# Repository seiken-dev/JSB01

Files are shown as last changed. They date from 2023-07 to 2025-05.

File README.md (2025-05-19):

# JSB01 -- Johann Sebastian Bachってなに？

<p align="center">
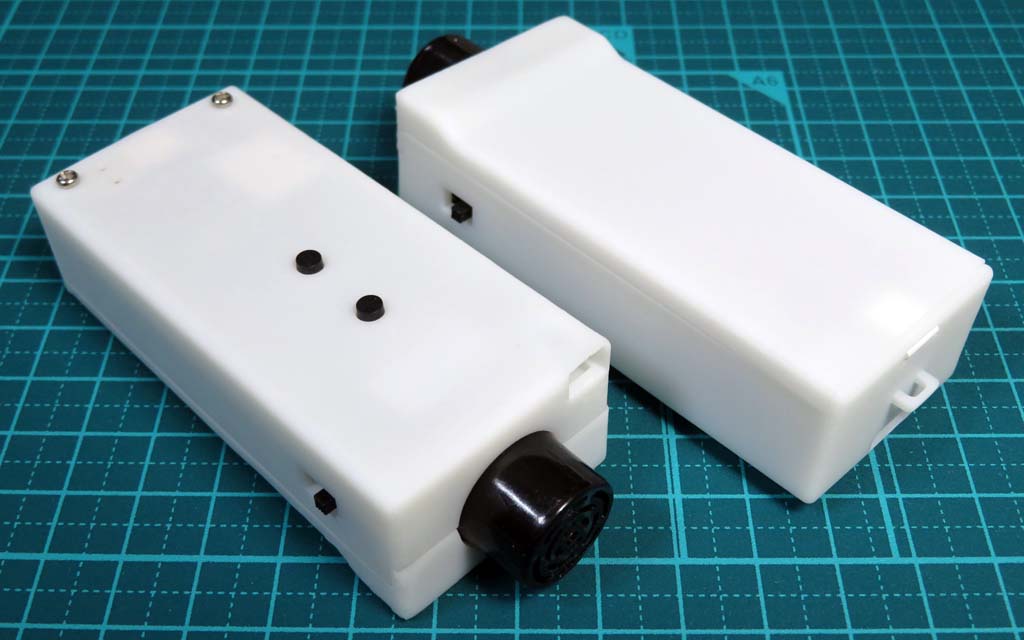
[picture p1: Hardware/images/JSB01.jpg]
JSB01

</p>

視覚障害者の歩行支援デバイスです。距離センサー、地磁気センサー(コンパス)、照度センサーを備え、振動によって情報を伝えます。

## コンテンツ
- **Firmware**<br>
PlatformIOでビルドできるソースコードです(動作テスト用)。[XIAO RP2040](https://wiki.seeedstudio.com/XIAO-RP2040/)(Rev.1)と、基板実装のRP2040(Rev.3)に対応しています。
- **KiCad**<br>
[KiCad](https://www.kicad.org/)のプロジェクトです。Rev.1の**JSB01.kicad_pro**と、Rev.3の**JSB01R3.kicad_pro**の２つのプロジェクトファイルがあります。シンボルとフットプリントは共通です。
- **Blender**<br>
3Dプリントケース作成用のBlenderのプロジェクトファイルと、発注に使用したSTLファイルです。

※ **KiCad**と**Blender**のデータは、**Creative Commons** [**CC BY**](https://creativecommons.org/licenses/by/4.0/legalcode.ja)のライセンスの元で、自由に使用/改変/製作して頂いて構いません。ただし、データや製作物に対しては作者は一切の責任を負いません。

## 各ブランチはなんのため？

* c.mos: c.mosさん作成のコードです。ハードウェアのすべての機能を実装しています
* ATtiny: ATtiny X0Xシリーズをマイコンとして使うブランチ
* ESP32C3: XIAO ESP32C3をマイコンとして使って、esp-idfを開発環境にするブランチ
* RP2040: RP2040あるいは XIAO RP2040を使って、pico-sdkを開発環境にするブランチ
* Experimental: 各種実験ブランチ
* main: そのうちメインになるだろうブランチ

## その他

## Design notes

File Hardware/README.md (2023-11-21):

# JSB01ハードウェア
<p align="center">
JSB01
</p>

視覚障害者の歩行支援デバイスです。距離センサー、地磁気センサー(コンパス)、照度センサーを備え、振動によって情報を伝えます。

# コンテンツ
- **KiCad**<br>
[KiCad](https://www.kicad.org/)のプロジェクトです。Rev.1の**JSB01.kicad_pro**と、Rev.3の**JSB01R3.kicad_pro**の２つのプロジェクトファイルがあります。シンボルとフットプリントは共通です。
- **Blender**<br>
3Dプリントケース作成用のBlenderのプロジェクトファイルと、発注に使用したSTLファイルです。

# 基板の組み立て(Rev.3)
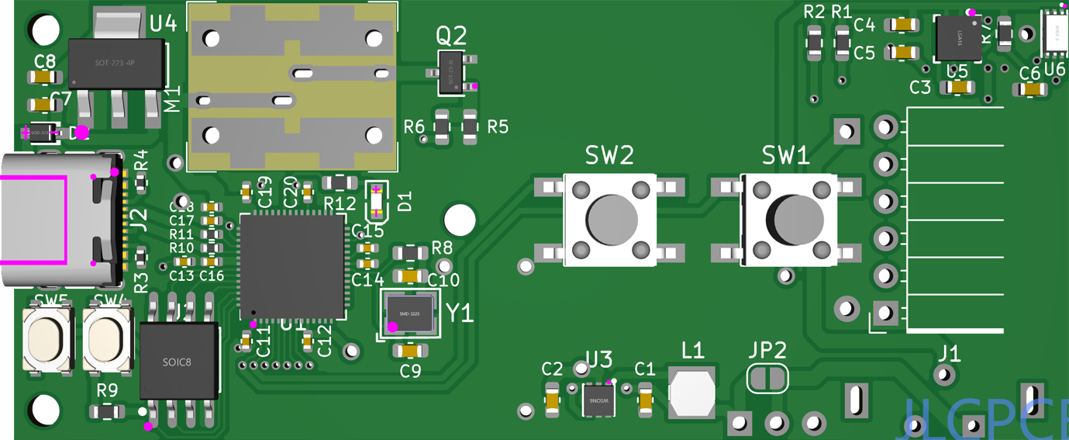
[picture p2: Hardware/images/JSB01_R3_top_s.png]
JSB01_R3_top_s
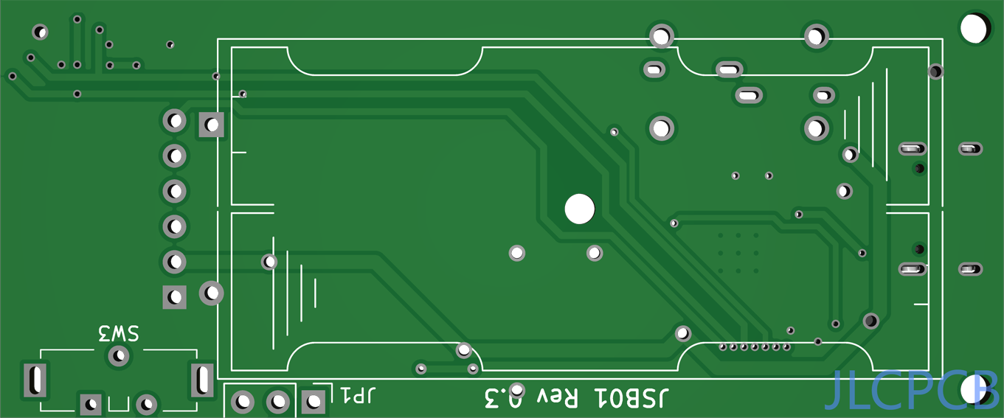
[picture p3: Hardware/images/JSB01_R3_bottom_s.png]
JSB01_R3_bottom_s
  

表面実装部品(SMD)は[JLCPCB](https://jlcpcb.com/)などPCB基板発注業者で実装できます。それ以外にはんだ付けする必要な部品のリストを載せます。

- [リニア振動アクチュエータ LD14](https://akizukidenshi.com/catalog/g/gP-06838/)<br>
こちらもSMDなので、基板業者へ部品を送って実装してもらうのがベストですが、手はんだの場合は、まずリード線をLD14の裏へはんだ付けした上で、リード線を基板の穴から引き出してはんだ付けして固定します。
- [L型ピンソケット(6P)](https://akizukidenshi.com/catalog/g/gC-09862/)<br>
MaxBotixの超音波センサー[MB10XXシリーズ](https://akizukidenshi.com/catalog/g/gM-08238/)を付けるソケットです。超音波センサーの基板側にも、GND～PW端子の6ピンに、ピンヘッダを付ける必要があります。
- [スライドスイッチ(ESD175202)](https://akizukidenshi.com/catalog/g/gP-08944/)
- [単4×2 電池ケース(SN4-2PC)](https://www.marutsu.co.jp/pc/i/65116/)

他に、電流測定用のJP1に3ピンヘッダを付けてジャンパピンを付けるか、JP2のソルダジャンパーをはんだで繋げます。<br>
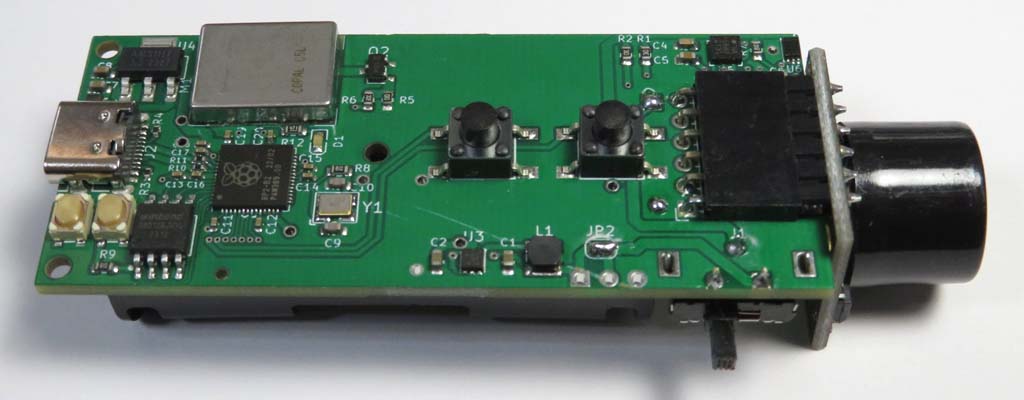
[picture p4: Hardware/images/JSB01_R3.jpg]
JSB01_R3


# 基板の組み立て(Rev.1)
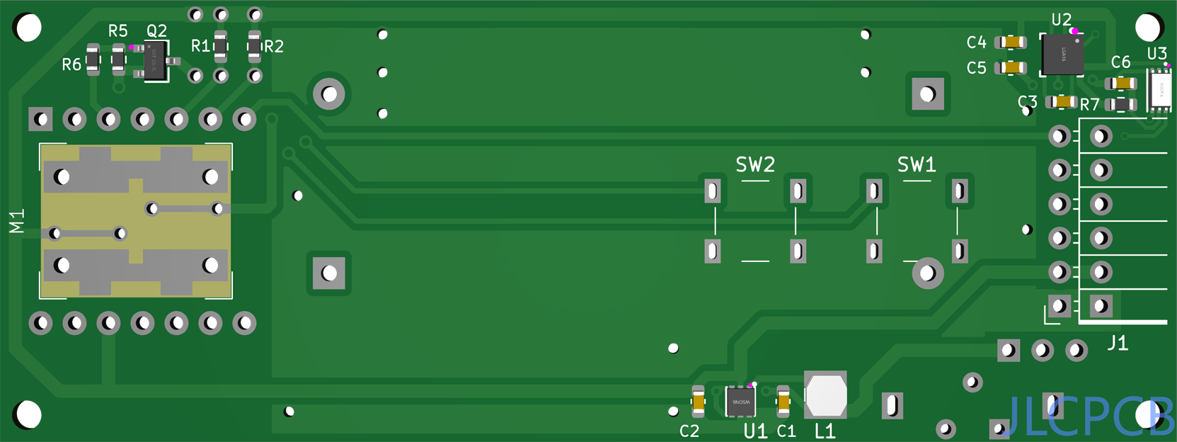
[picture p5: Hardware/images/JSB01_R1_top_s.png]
JSB01_R1_top_s
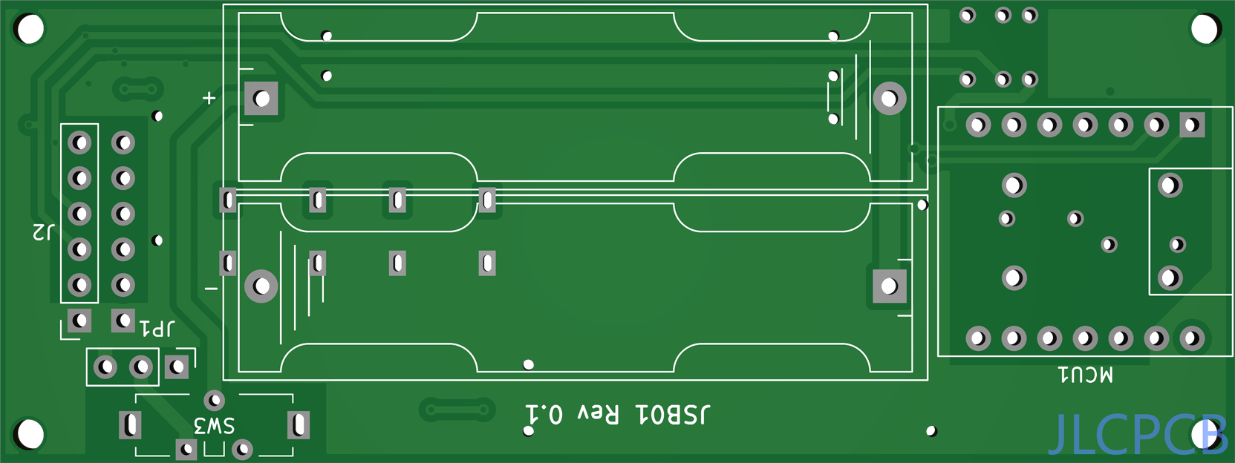
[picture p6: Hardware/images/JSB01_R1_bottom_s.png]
JSB01_R1_bottom_s
  

最初に作った基板です。リビジョンが跳んでいるのは、Rev.2から3Dプリントケースを作ったためで、設計した基板はこの２種類だけです。これは[キャンドゥのケース](https://ec.cando-web.co.jp/item/4582547004810/)に収めるサイズで作りました。[Seeed Studio XIAO](https://wiki.seeedstudio.com/SeeedStudio_XIAO_Series_Introduction/)シリーズが載るソケットと、超音波センサーの他に[ストロベリーリナックス](https://strawberry-linux.com)の[TOFセンサー](https://strawberry-linux.com/catalog/items?code=15311)を付けられます。Rev.3以外に必要な部品のリストを載せます。
- [XIAO RP2040](https://wiki.seeedstudio.com/XIAO-RP2040/)<br>
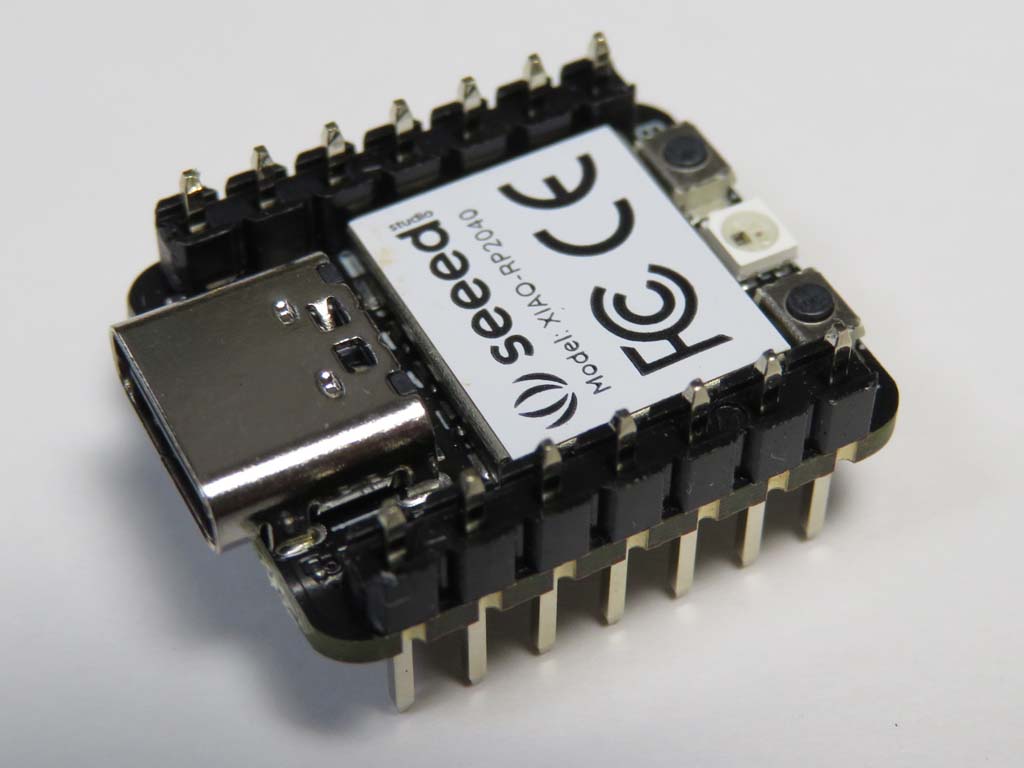
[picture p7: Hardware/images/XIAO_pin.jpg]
XIAO_pin
<br>
高さを低く収めるために、上からピンヘッダを差し込んではんだ付けします。
- [TOFセンサー](https://strawberry-linux.com/catalog/items?code=15311)<br>
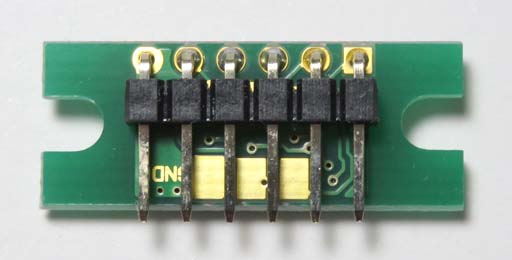
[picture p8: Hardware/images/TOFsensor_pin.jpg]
TOFsensor_pin
<br>
このように、上下逆向きにして裏に[L型ピンヘッダ](https://akizukidenshi.com/catalog/g/gC-12985/)を付けます。
- [シングルピンソケット(低メス)](https://akizukidenshi.com/catalog/g/gC-03138/)<br>
XIAO RP2040とTOFセンサーを載せるために使います。
- [タクトスイッチ×2](https://akizukidenshi.com/catalog/g/gP-03647/)
- [単4電池ボックス×2](https://akizukidenshi.com/catalog/g/gP-02670/)
<br>
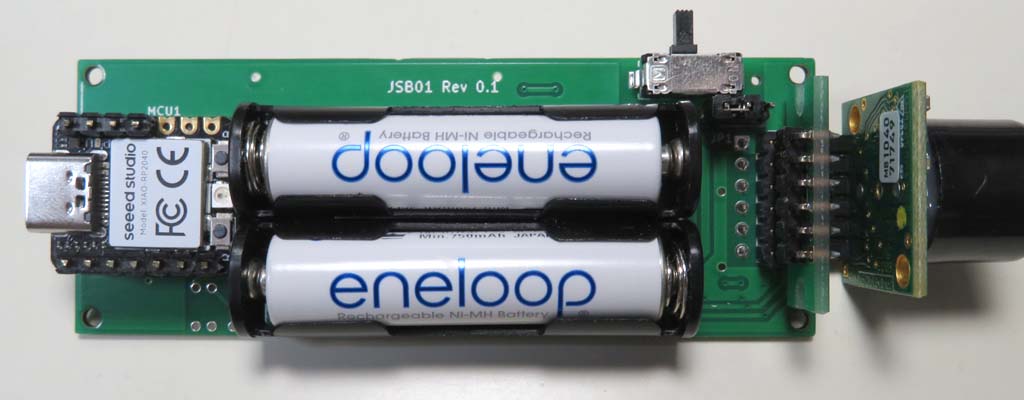
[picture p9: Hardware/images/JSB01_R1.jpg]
JSB01_R1


# 3Dプリントケース
R2(r2)がRev.1基板用、R3(r3)がRev.3基板用のケースです。Rev.1用ケースでは、照度センサー用の穴をチップの上面に開けていましたが、Rev.3では凹面鏡の様に加工して前方からの光を取り入れるようにしました。そのため、凹面鏡の部分を[メタリックの塗料](https://www.mr-hobby.com/ja/product1/category_10/3670.html)で塗る必要があります。

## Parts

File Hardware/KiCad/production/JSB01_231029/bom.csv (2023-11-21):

Designator | Footprint | Quantity | Value | LCSC Part #
C1, C7, C8 | 0603 | 3 | 10uF | C19702
C10, C9 | 0603 | 2 | 33p | C1663
C11, C12, C13, C14, C15, C16, C17, C18, C19, C20 | 0402 | 10 | 100n | C307331
C2 | 0603 | 1 | 22uF | C59461
C3 | 0603 | 1 | 0.22uF | C21120
C4 | 0603 | 1 | 0.1uF | C14663
C5 | 0603 | 1 | 4.7uF | C19666
C6 | 0603 | 1 | 1uF | C15849
D1 | LED0603-RD_GREEN | 1 | LED | C510026
D2 | SOD-323_L1.8-W1.3-LS2.5-RD | 1 | NSR0320MW2T1G | C48192
J1 | PinSocket_1x06_P2.54mm_Horizontal | 1 | MB10XX Sonar
J2 | USB-C-SMD_TYPE-C-16P-1 | 1 | USB_C_Receptacle_USB2.0 | C2982555
JP2 | SolderJumper-2_P1.3mm_Open_RoundedPad1.0x1.5mm | 1 | SolderJumper_2_Open
L1 | IND-SMD_L3.0-W3.0_VLS3010ET | 1 | 3.3μH | C136236
Q2 | AO3400A | 1 | AO3400A | C20917
R1, R2 | 0603 | 2 | 10KΩ | C25804
R10, R11 | 0402 | 2 | 27.4 | C274349
R12 | 0603 | 1 | 470 | C23179
R3, R4 | 0402 | 2 | 5.1K | C25905
R5 | 0603 | 1 | 100KΩ | C25803
R6 | 0603 | 1 | 20KΩ | C4184
R7, R8, R9 | 0603 | 3 | 1K | C21190
SW1, SW2 | Tactile Switch_SMD | 2 | Tactile | C294566
SW4, SW5 | KEY-SMD_4P-L4.2-W3.2 | 2 | SKRPABE010 | C115360
U1 | RP2040-QFN-56 | 1 | RP2040 | C2040
U2 | SOP-8-208mil | 1 | W25Q128JVSIQ
U3 | WSON-6_L2.0-W2.0-P0.65-BL-EP | 1 | TPS61291DRVR | C464809
U4 | SOT-223-3_L6.5-W3.4 | 1 | AMS1117-3.3 | C6186
U5 | LGA-16_L3.0-W3.0-P0.50-BL_SQ | 1 | QMC5883L(0x0D) | C976032
U6 | WSOF-6_L2.6-W1.6-P0.50-TL-EP | 1 | BH1750FVI(0x23) | C78960
Y1 | OSC-SMD_4P-L3.2-W2.5 | 1 | TAXM12M4RLBDDT2T

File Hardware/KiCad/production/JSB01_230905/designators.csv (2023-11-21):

BT1:1
C1:1
C2:1
C3:1
C4:1
C5:1
C6:1
J1:1
J2:1
JP1:1
L1:1
M1:1
MCU1:1
Pad:6
Q2:1
R1:1
R2:1
R5:1
R6:1
R7:1
REF**:4
SW1:1
SW2:1
SW3:1
U1:1
U2:1
U3:1

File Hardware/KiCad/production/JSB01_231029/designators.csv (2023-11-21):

BT1:1
C1:1
C10:1
C11:1
C12:1
C13:1
C14:1
C15:1
C16:1
C17:1
C18:1
C19:1
C2:1
C20:1
C3:1
C4:1
C5:1
C6:1
C7:1
C8:1
C9:1
D1:1
D2:1
J1:1
J2:1
JP1:1
JP2:1
L1:1
M1:1
Q2:1
R1:1
R10:1
R11:1
R12:1
R2:1
R3:1
R4:1
R5:1
R6:1
R7:1
R8:1
R9:1
REF**:2
SW1:1
SW2:1
SW3:1
SW4:1
SW5:1
U1:1
U2:1
U3:1
U4:1
U5:1
U6:1
Y1:1

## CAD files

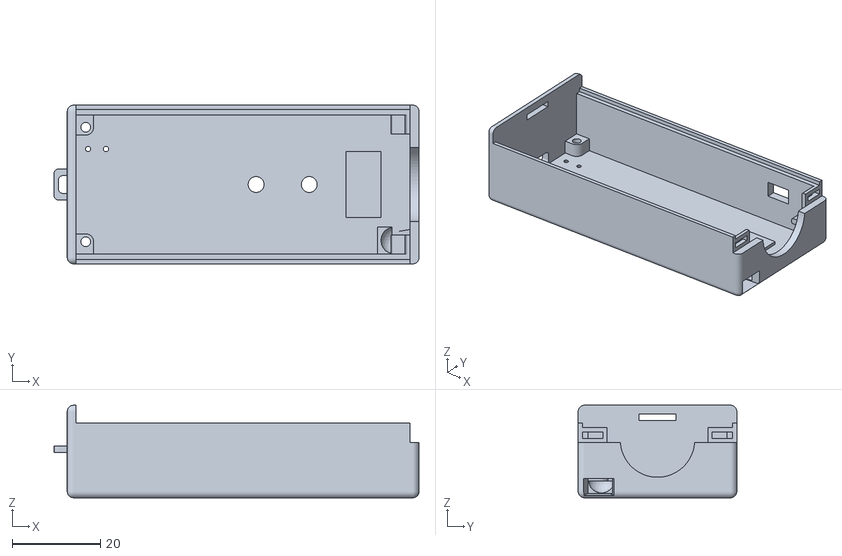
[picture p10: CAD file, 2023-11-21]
Hardware/Blender/JSB01_caseR31.stl
82.8 x 36.0 x 21.0

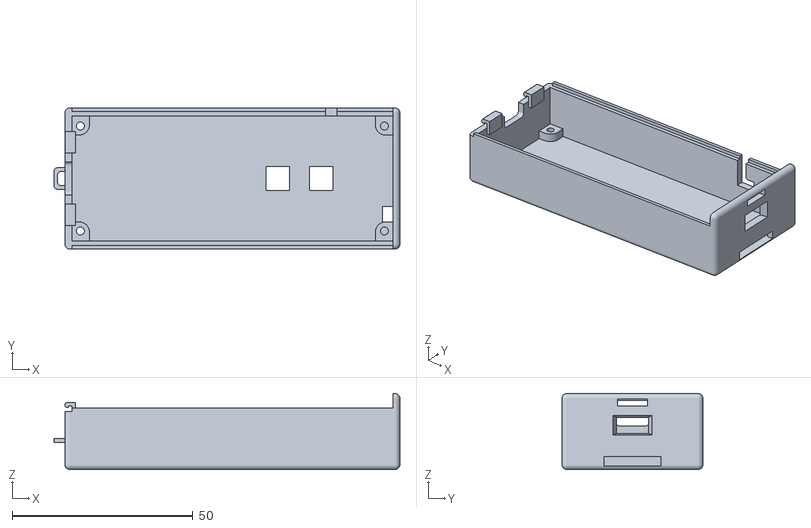
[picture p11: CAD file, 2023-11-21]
Hardware/Blender/JSB01_caseR21.stl
95.6 x 39.0 x 21.0

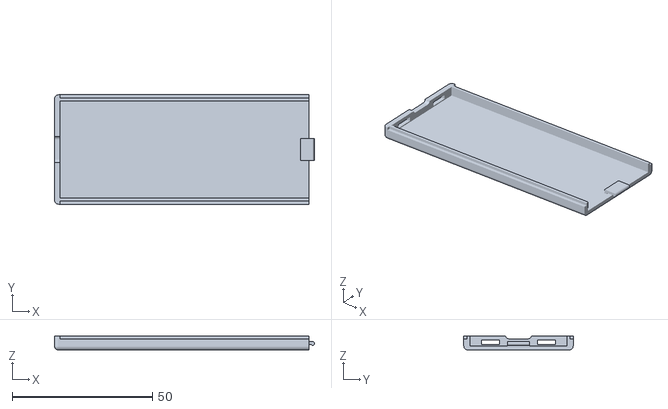
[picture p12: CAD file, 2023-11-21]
Hardware/Blender/JSB01_casetopR2.stl
92.6 x 39.0 x 5.00

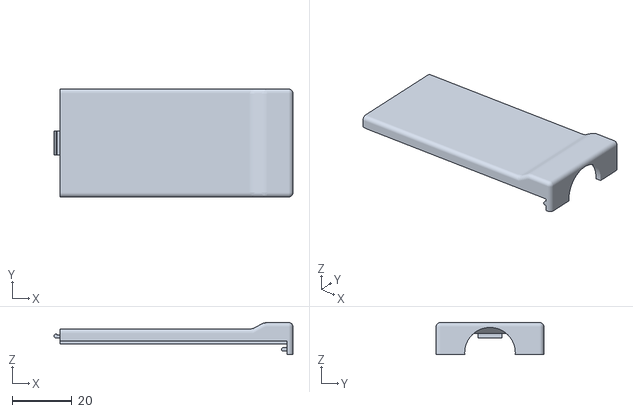
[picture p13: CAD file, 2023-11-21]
Hardware/Blender/JSB01_casetopR31.stl
79.8 x 36.0 x 10.7

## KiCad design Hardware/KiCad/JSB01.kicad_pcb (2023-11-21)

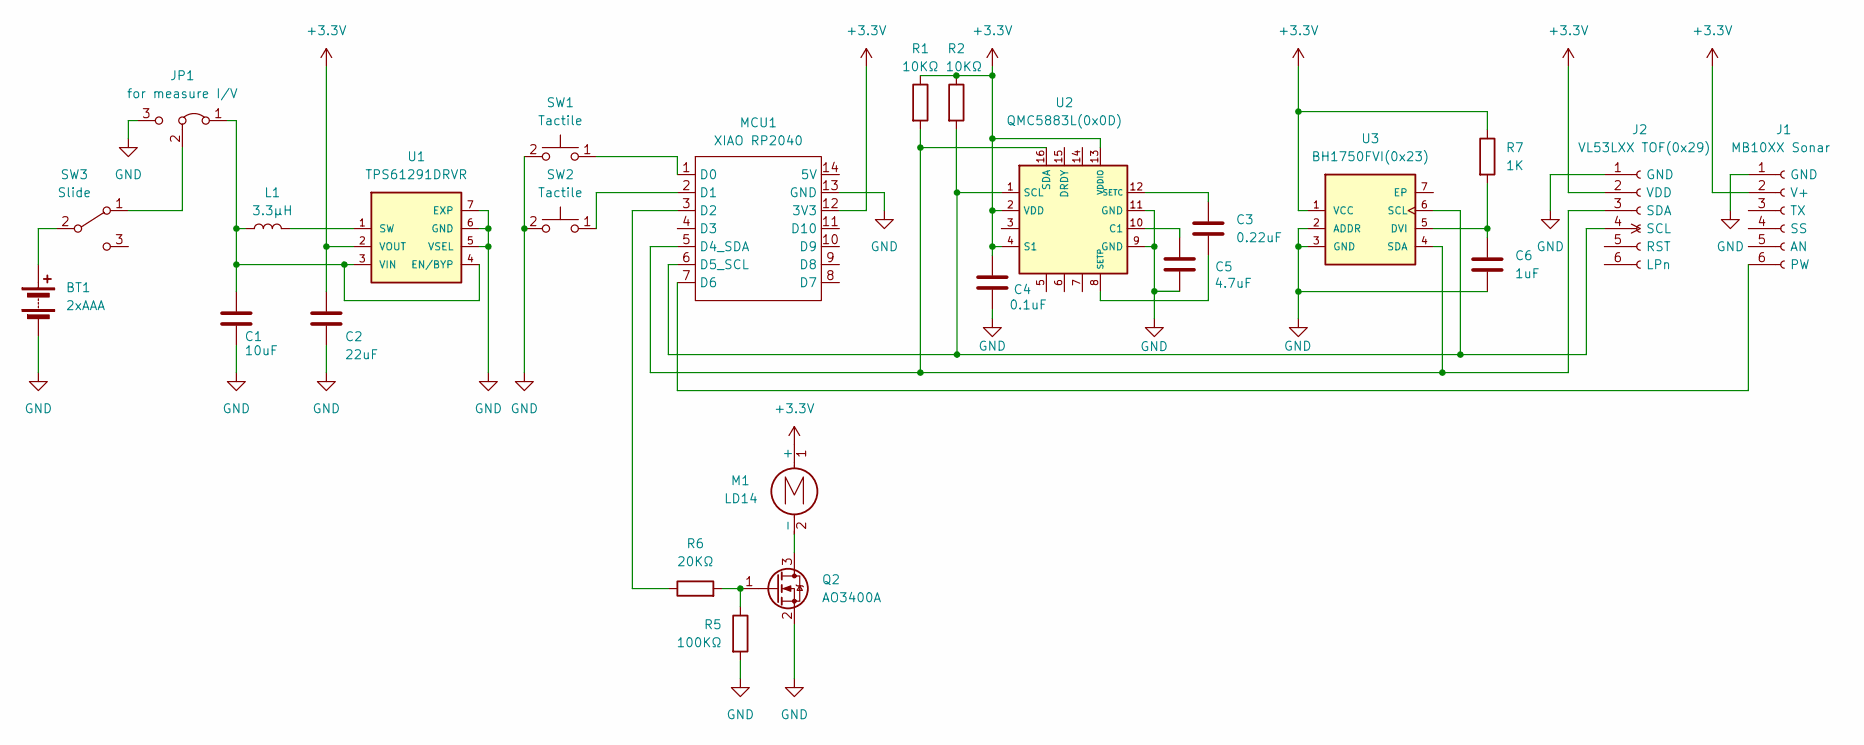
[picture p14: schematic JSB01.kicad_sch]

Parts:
BT1: 2xAAA; BatteryHolder 2xAAA
C1: 10uF; C_0603_1608Metric; LCSC C19702
C2: 22uF; C_0603_1608Metric; LCSC C59461
C3: 0.22uF; C_0603_1608Metric; LCSC C21120
C4: 0.1uF; C_0603_1608Metric; LCSC C14663
C5: 4.7uF; C_0603_1608Metric; LCSC C19666
C6: 1uF; C_0603_1608Metric; LCSC C15849
J1: MB10XX Sonar; PinSocket_1x06_P2.54mm_Horizontal
J2: VL53LXX TOF(0x29); PinSocket_1x06_P2.54mm_Vertical
JP1: for measure I/V; Jumper_1x03_P2.54mm
L1: 3.3μH; IND-SMD_L3.0-W3.0_VLS3010ET; LCSC C136236
M1: LD14
MCU1: XIAO RP2040; MOUDLE14P-2.54-21X17.8MM
Q2: AO3400A; SOT-23; LCSC C20917
R1, R2: 10KΩ; R_0603_1608Metric; LCSC C25804
R5: 100KΩ; R_0603_1608Metric; LCSC C25803
R6: 20KΩ; R_0603_1608Metric; LCSC C4184
R7: 1K; R_0603_1608Metric; LCSC C21190
SW1, SW2: Tactile; SW_tactile_DTS6
SW3: Slide; SW_Slide_ESD1752
U1: TPS61291DRVR; WSON-6_L2.0-W2.0-P0.65-BL-EP; LCSC C464809
U2: QMC5883L(0x0D); LGA-16_L3.0-W3.0-P0.50-BL_SQ; LCSC C976032
U3: BH1750FVI(0x23); WSOF-6_L2.6-W1.6-P0.50-TL-EP; LCSC C78960

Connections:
+3.3V: C2.1, C4.1, J1.2 (V+), J2.2 (VDD), M1.1 (+), MCU1.12 (3V3), R1.1, R2.1, R7.1, U1.2 (VOUT), U2.2 (VDD), U2.4 (S1), U2.13 (VDDIO), U3.1 (VCC)
GND: BT1.2 (-), C1.2, C2.2, C4.2, C5.2, C6.2, J1.1 (GND), J2.1 (GND), JP1.3 (B), MCU1.13 (GND), Q2.2 (S), R5.2, SW1.2, SW2.2, U1.5 (VSEL), U1.6 (GND), U1.7 (EXP), U2.9 (GND), U2.11 (GND), U3.2 (ADDR), U3.3 (GND)
unnamed: BT1.1 (+), SW3.2 (B)
unnamed: J1.6 (PW), MCU1.7 (D6)
unnamed: J2.4 (SCL), MCU1.6 (D5_SCL), R2.2, U2.1 (SCL), U3.6 (SCL)
unnamed: J2.3 (SDA), MCU1.5 (D4_SDA), R1.2, U2.16 (SDA), U3.4 (SDA)
unnamed: C1.1, JP1.1 (A), L1.1, U1.3 (VIN), U1.4 (EN/BYP)
unnamed: JP1.2 (C), SW3.1 (A)
unnamed: M1.2 (-), Q2.3 (D)
unnamed: MCU1.1 (D0), SW1.1
unnamed: MCU1.2 (D1), SW2.1
unnamed: MCU1.3 (D2), R6.1
unnamed: Q2.1 (G), R5.1, R6.2
unnamed: L1.2, U1.1 (SW)
unnamed: C5.1, U2.10 (C1)
unnamed: C3.1, U2.12 (SETC)
unnamed: C3.2, U2.8 (SETP)
unnamed: C6.1, R7.2, U3.5 (DVI)

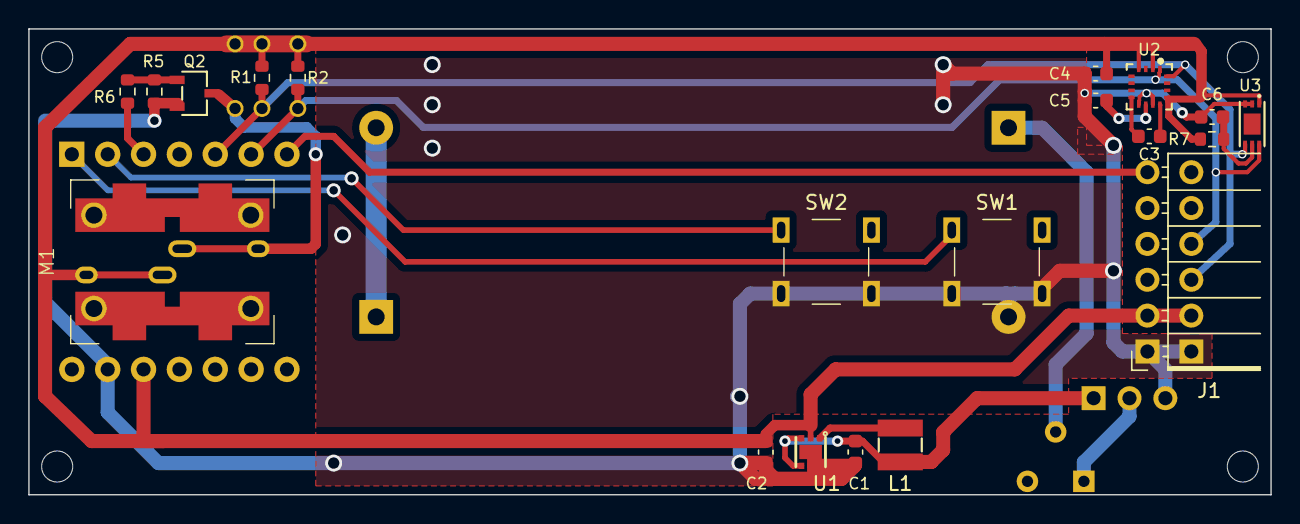
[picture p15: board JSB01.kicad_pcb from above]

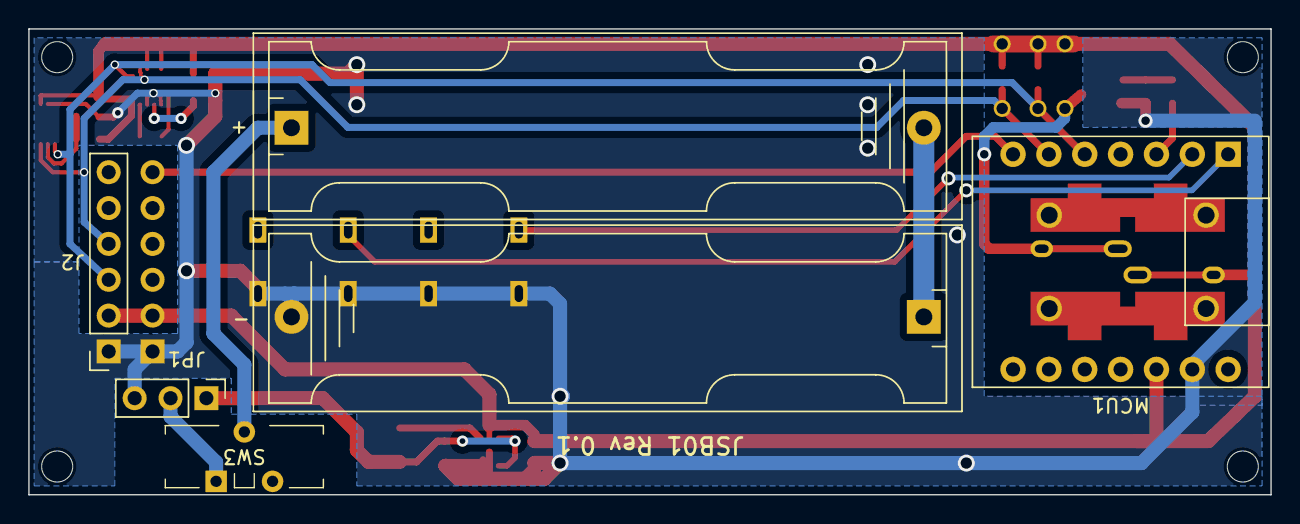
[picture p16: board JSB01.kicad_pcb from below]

Board: 2 copper layers, 88.0 x 33.0 mm, 31 parts (5 on the bottom side), 18 nets.

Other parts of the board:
Pad: Pad1.2_0.8
Pad#2, Pad#3, Pad#4, Pad#5, Pad#6: Pad1.2_0.8

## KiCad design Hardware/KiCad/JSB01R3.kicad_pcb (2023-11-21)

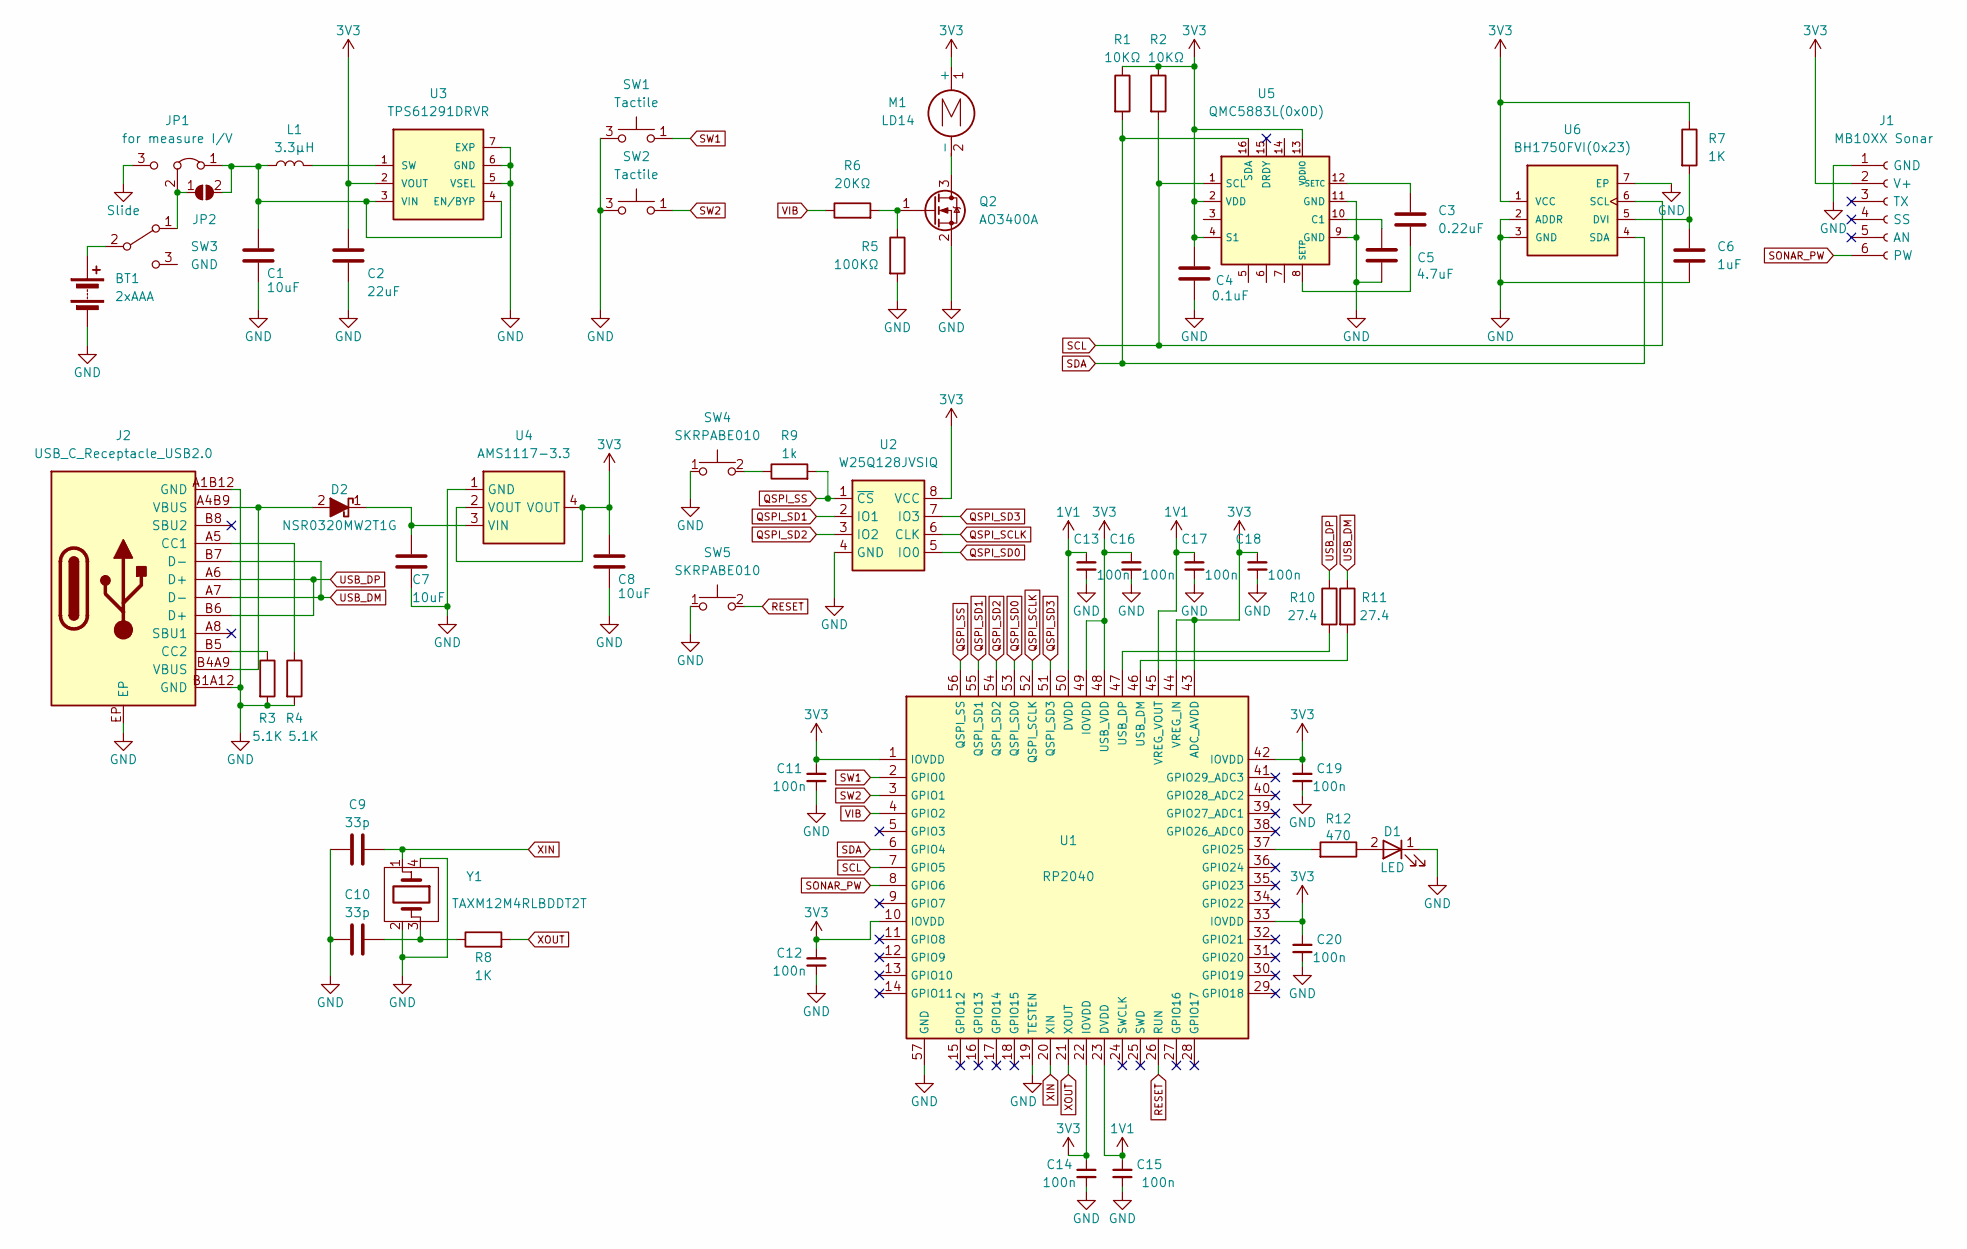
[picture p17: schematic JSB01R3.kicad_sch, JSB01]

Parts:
BT1: 2xAAA; BatteryHolder SN4-2PC
C1, C7, C8: 10uF; C_0603_1608Metric; LCSC C19702
C2: 22uF; C_0603_1608Metric; LCSC C59461
C3: 0.22uF; C_0603_1608Metric; LCSC C21120
C4: 0.1uF; C_0603_1608Metric; LCSC C14663
C5: 4.7uF; C_0603_1608Metric; LCSC C19666
C6: 1uF; C_0603_1608Metric; LCSC C15849
C9, C10: 33p; C_0603_1608Metric; LCSC C1663
C11, C12, C13, C14, C15, C16, C17, C18, C19, C20: 100n; C_0402_1005Metric; LCSC C307331
D1: LED; LED0603-RD_GREEN; LCSC C510026
D2: NSR0320MW2T1G; SOD-323_L1.8-W1.3-LS2.5-RD; LCSC C48192
J1: MB10XX Sonar; PinSocket_1x06_P2.54mm_Horizontal
J2: USB_C_Receptacle_USB2.0; USB-C-SMD_TYPE-C-16P-1; LCSC C2982555
JP1: for measure I/V; Jumper_1x03_P2.54mm
JP2: SolderJumper_2_Open; SolderJumper-2_P1.3mm_Open_RoundedPad1.0x1.5mm
L1: 3.3μH; IND-SMD_L3.0-W3.0_VLS3010ET; LCSC C136236
M1: LD14
Q2: AO3400A; LCSC C20917
R1, R2: 10KΩ; R_0603_1608Metric; LCSC C25804
R3, R4: 5.1K; R_0402_1005Metric; LCSC C25905
R5: 100KΩ; R_0603_1608Metric; LCSC C25803
R6: 20KΩ; R_0603_1608Metric; LCSC C4184
R7, R8: 1K; R_0603_1608Metric; LCSC C21190
R9: 1k; R_0603_1608Metric; LCSC C21190
R10, R11: 27.4; R_0402_1005Metric; LCSC C274349
R12: 470; R_0603_1608Metric; LCSC C23179
SW1, SW2: Tactile; Tactile Switch_SMD; LCSC C294566
SW3: Slide; SW_Slide_ESD1752
SW4, SW5: SKRPABE010; KEY-SMD_4P-L4.2-W3.2; LCSC C115360
U1: RP2040; RP2040-QFN-56; LCSC C2040
U2: W25Q128JVSIQ; SOP-8-208mil; LCSC C97521
U3: TPS61291DRVR; WSON-6_L2.0-W2.0-P0.65-BL-EP; LCSC C464809
U4: AMS1117-3.3; SOT-223-3_L6.5-W3.4; LCSC C6186
U5: QMC5883L(0x0D); LGA-16_L3.0-W3.0-P0.50-BL_SQ; LCSC C976032
U6: BH1750FVI(0x23); WSOF-6_L2.6-W1.6-P0.50-TL-EP; LCSC C78960
Y1: TAXM12M4RLBDDT2T; OSC-SMD_4P-L3.2-W2.5; LCSC C133334

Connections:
+1V1: C13.1, C15.1, C17.1, U1.23 (DVDD), U1.45 (VREG_VOUT), U1.50 (DVDD)
+3V3: C2.1, C4.1, C8.1, C11.1, C12.1, C14.1, C16.1, C18.1, C19.1, C20.1, J1.2 (V+), M1.1 (+), R1.1, R2.1, R7.1, U1.1 (IOVDD), U1.10 (IOVDD), U1.22 (IOVDD), U1.33 (IOVDD), U1.42 (IOVDD), U1.43 (ADC_AVDD), U1.44 (VREG_IN), U1.48 (USB_VDD), U1.49 (IOVDD), U2.8 (VCC), U3.2 (VOUT), U4.2 (VOUT), U4.4 (VOUT), U5.2 (VDD), U5.4 (S1), U5.13 (VDDIO), U6.1 (VCC)
GND: BT1.2 (-), C1.2, C2.2, C4.2, C5.2, C6.2, C7.2, C8.2, C9.1, C10.1, C11.2, C12.2, C13.2, C14.2, C15.2, C16.2, C17.2, C18.2, C19.2, C20.2, D1.1 (K), J1.1 (GND), J2.A1B12 (GND), J2.B1A12 (GND), J2.EP, JP1.3 (B), Q2.2 (S), R3.2, R4.2, R5.2, SW1.3, SW1.4, SW2.3, SW2.4, SW4.1, SW5.1, U1.19 (TESTEN), U1.57 (GND), U2.4 (GND), U3.5 (VSEL), U3.6 (GND), U3.7 (EXP), U4.1 (GND), U5.9 (GND), U5.11 (GND), U6.2 (ADDR), U6.3 (GND), U6.7 (EP), Y1.2 (GND), Y1.4 (GND)
unnamed: BT1.1 (+), SW3.2 (B)
unnamed: D1.2 (A), R12.1
unnamed: D2.2 (A), J2.A4B9 (VBUS), J2.B4A9 (VBUS)
unnamed: C7.1, D2.1 (K), U4.3 (VIN)
unnamed: J2.A5 (CC1), R4.1
unnamed: J2.B5 (CC2), R3.1
unnamed: C1.1, JP1.1 (A), JP2.2 (B), L1.1, U3.3 (VIN), U3.4 (EN/BYP)
unnamed: JP1.2 (C), JP2.1 (A), SW3.1 (A)
unnamed: M1.2 (-), Q2.3 (D)
unnamed: Q2.1 (G), R5.1, R6.2
unnamed: R9.1, SW4.2
unnamed: R12.2, U1.37 (GPIO25)
unnamed: R11.2, U1.46 (USB_DM)
unnamed: R10.2, U1.47 (USB_DP)
unnamed: L1.2, U3.1 (SW)
unnamed: C5.1, U5.10 (C1)
unnamed: C3.1, U5.12 (SETC)
unnamed: C3.2, U5.8 (SETP)
unnamed: C6.1, R7.2, U6.5 (DVI)
unnamed: C10.2, R8.1, Y1.3 (OSC2)
QSPI_SCLK: U1.52 (QSPI_SCLK), U2.6 (CLK)
QSPI_SD0: U1.53 (QSPI_SD0), U2.5 (IO0)
QSPI_SD1: U1.55 (QSPI_SD1), U2.2 (IO1)
QSPI_SD2: U1.54 (QSPI_SD2), U2.3 (IO2)
QSPI_SD3: U1.51 (QSPI_SD3), U2.7 (IO3)
QSPI_SS: R9.2, U1.56 (QSPI_SS), U2.1 (~CS)
RESET: SW5.2, U1.26 (RUN)
SCL: R2.2, U1.7 (GPIO5), U5.1 (SCL), U6.6 (SCL)
SDA: R1.2, U1.6 (GPIO4), U5.16 (SDA), U6.4 (SDA)
SONAR_PW: J1.6 (PW), U1.8 (GPIO6)
SW1: SW1.1, SW1.2, U1.2 (GPIO0)
SW2: SW2.1, SW2.2, U1.3 (GPIO1)
USB_DM: J2.A7 (D-), J2.B7 (D-), R11.1
USB_DP: J2.A6 (D+), J2.B6 (D+), R10.1
VIB: R6.1, U1.4 (GPIO2)
XIN: C9.2, U1.20 (XIN), Y1.1 (OSC1)
XOUT: R8.2, U1.21 (XOUT)

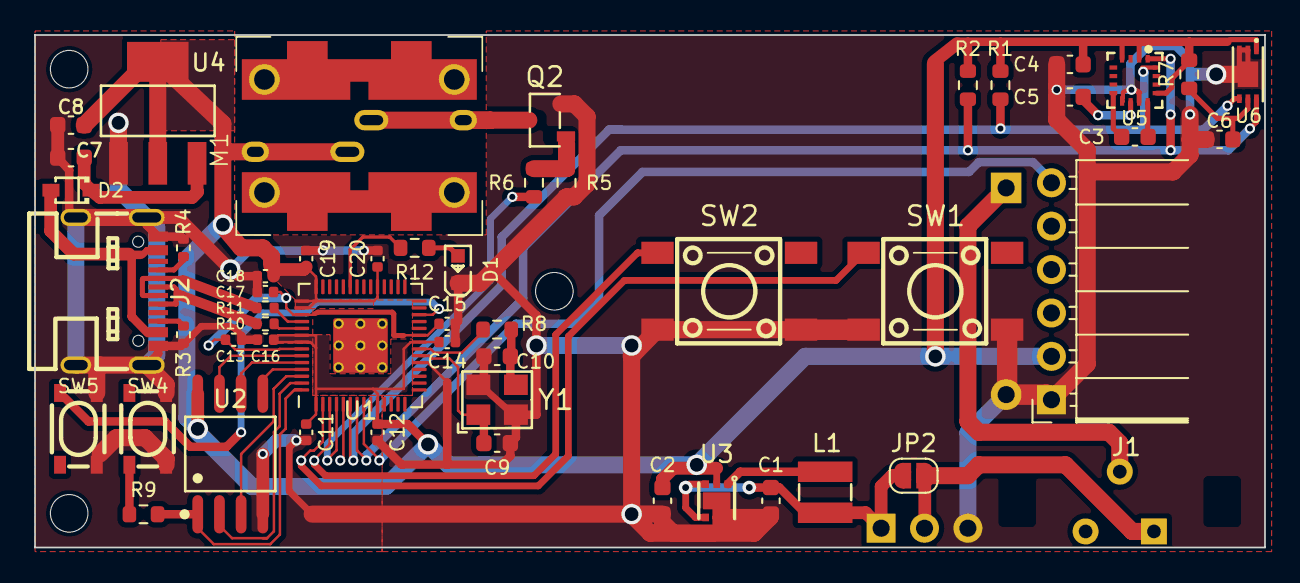
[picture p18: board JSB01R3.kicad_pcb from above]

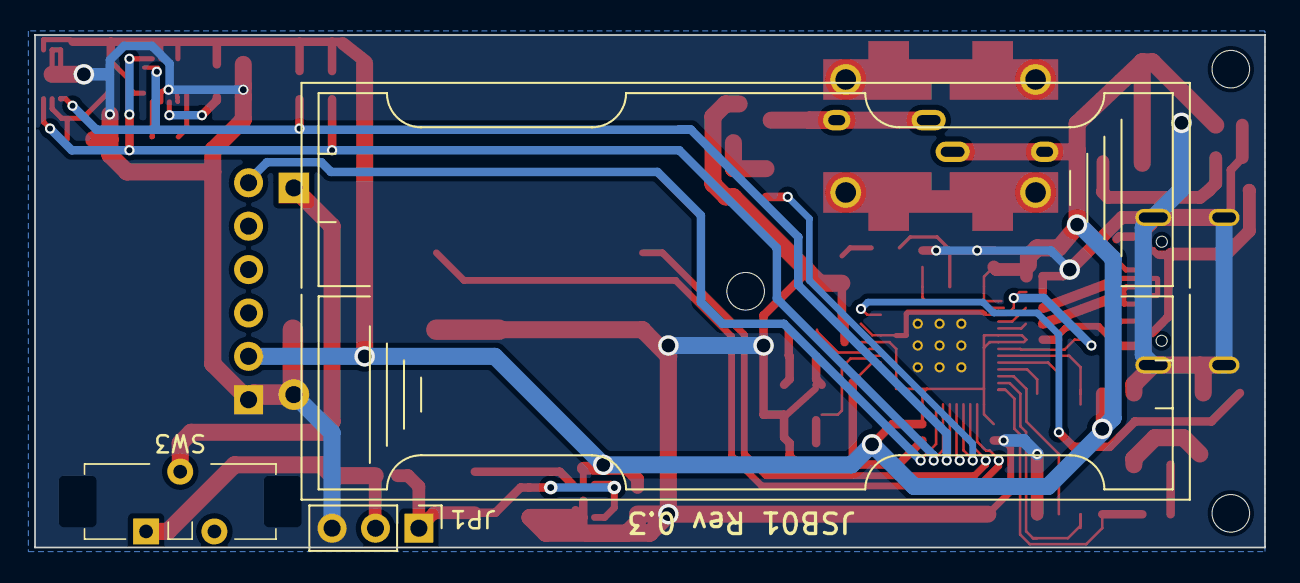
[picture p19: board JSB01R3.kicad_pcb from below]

Board: 2 copper layers, 72.0 x 30.0 mm, 54 parts (3 on the bottom side), 40 nets.

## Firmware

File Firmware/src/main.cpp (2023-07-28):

#include <Arduino.h>
#include <cstdint>
constexpr uint8_t pin_sonar = D5;
constexpr uint8_t pin_button1 = D0;
constexpr uint8_t pin_button2 = D1;
constexpr uint8_t pin_vibe = D2;

constexpr uint8_t flash_ms = 10;

void flash(uint16_t ms = flash_ms) {
  digitalWrite(pin_vibe, HIGH);
  delay(ms);
  digitalWrite(pin_vibe, LOW);
}

void setup() {
  Serial.begin(115200);
  delay(500);
  Serial.println("start");
  pinMode(pin_sonar, INPUT);
  pinMode(pin_button1, INPUT_PULLUP);
  pinMode(pin_button2, INPUT_PULLUP);
  pinMode(pin_vibe, OUTPUT);
  delay(400); // wait USB Serial
  flash();;
  delay(100);
  flash();
}

uint16_t ranging()
{
  uint32_t time = pulseIn(pin_sonar, HIGH, 200*1000);
  return (time > 10*147) ? uint16_t(time/147) : 0;
}
void loop() {
  uint16_t distance = ranging();
  if (distance < 80) flash();
}

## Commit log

2023-07-19 * First commit. ビルドできないよお。
2023-07-28 * ビルド関係のファイルをgit管理から外した。
2023-07-28 * ひたすら距離を測るだけ。眼の前の障害物に対して、どの程度の反応ができるかをテストするためのコード。
2023-07-28 * readme書きました。
2023-11-16 * ディレクトリ構成を変更。
2023-11-21 * ハードウェアの作成プロジェクトファイルを追加。
    [JSB01.kicad_pcb, JSB01.kicad_sch, JSB01R3.kicad_pcb, JSB01R3.kicad_sch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]
2024-01-09 * ウェブサイト公開準備
2024-01-09 * ウェブサイトのソースディレクトリを変更
2024-01-09 * GitHub pagesの設定を一時的に削除
2024-01-09 * GitHub pagesのテスト中
